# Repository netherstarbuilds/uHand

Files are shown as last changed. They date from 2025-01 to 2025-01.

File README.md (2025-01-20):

# uHand inspired and powered by uMyo

uHand is a full hand manipulator and wrist but not a forearm. uhand requires the user to adapt the WristBracket.SLDPRT file to fit the forearm design they are using. This is as individuals have different amputations and forearm shapes making it not possible to design a one size fits all mount that would work well with this many degrees of freedom. uHand was not made by UltimateRobotics, but was designed to work with their incredible uMyo EMG sensor. uHand requires seven driver motors.

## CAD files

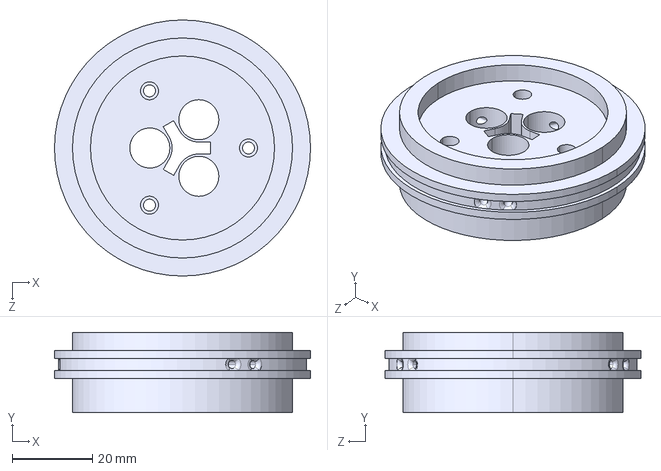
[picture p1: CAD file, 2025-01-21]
mainring.STEP
64.0 x 20.0 x 64.0 mm

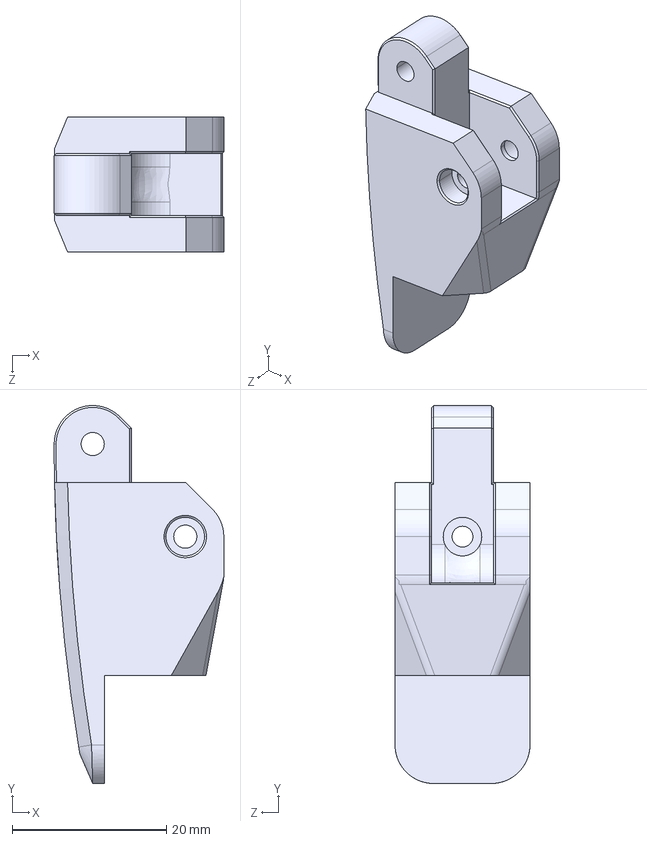
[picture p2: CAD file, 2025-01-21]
DISTAL2T.STEP
22.0 x 49.0 x 17.5 mm

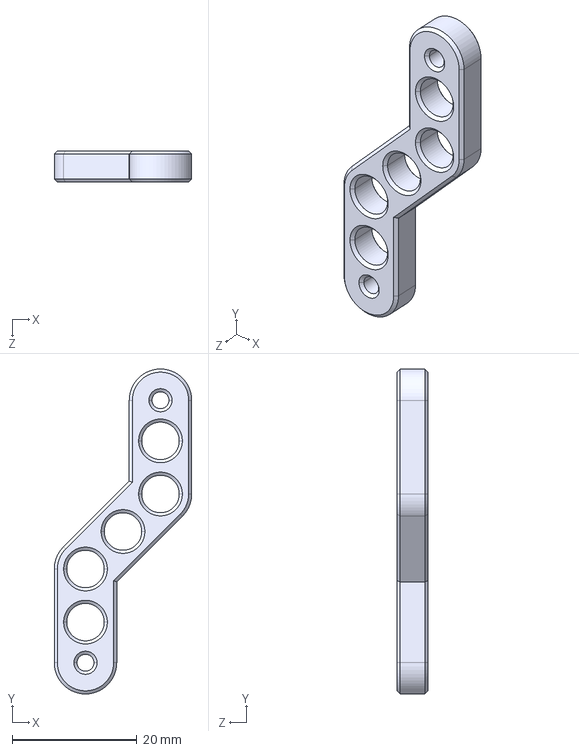
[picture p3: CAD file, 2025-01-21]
crosslinkP1bSTEEL.STEP
22.0 x 52.0 x 5.00 mm

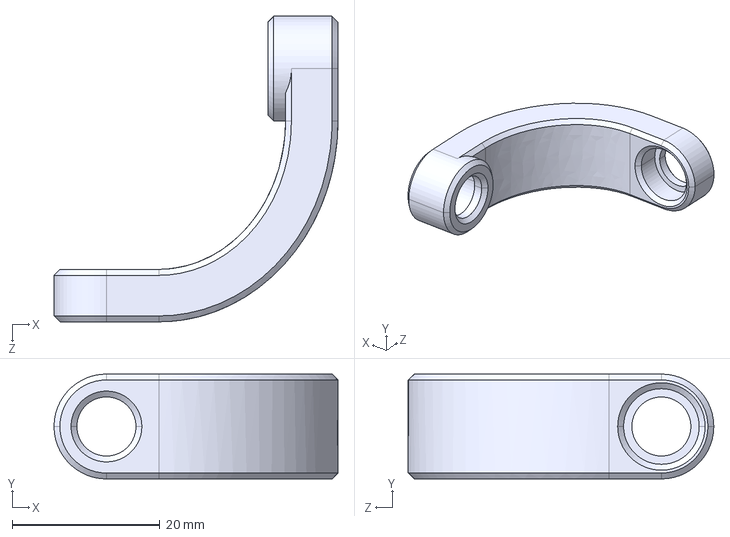
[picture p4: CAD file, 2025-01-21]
SPMbar.STEP
38.5 x 14.2 x 41.4 mm

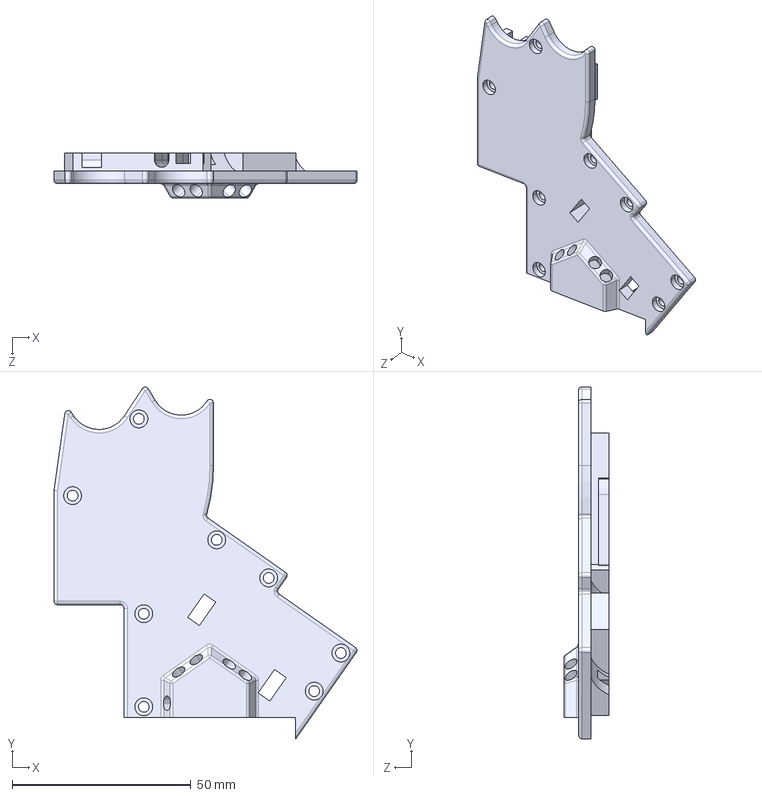
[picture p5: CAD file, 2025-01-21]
PalmPlate.STEP
84.6 x 98.4 x 12.6 mm

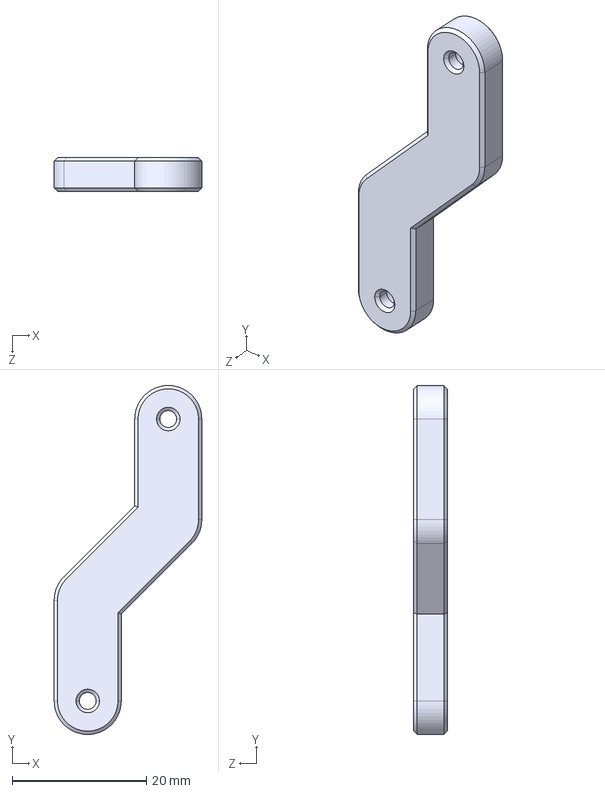
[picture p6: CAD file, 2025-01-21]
crosslinkP1a.STEP
22.0 x 52.0 x 5.00 mm

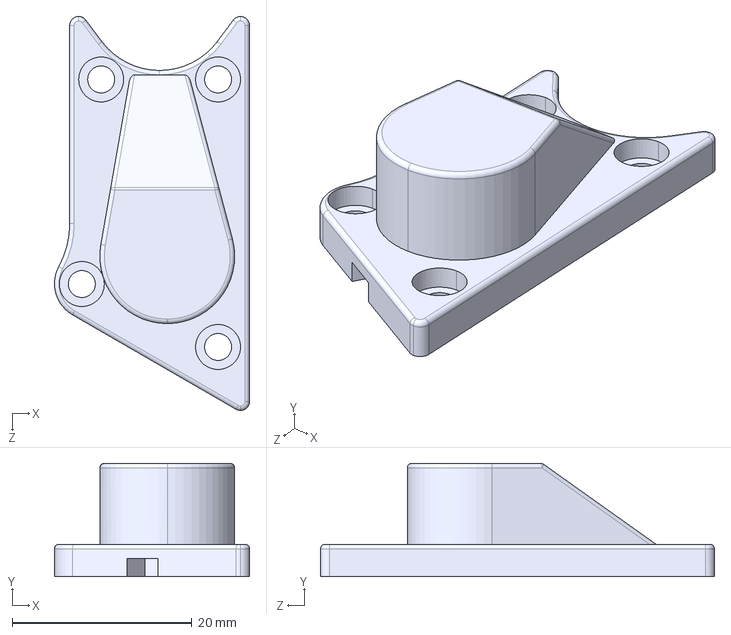
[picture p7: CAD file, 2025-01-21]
metacover.STEP
21.7 x 12.6 x 43.8 mm

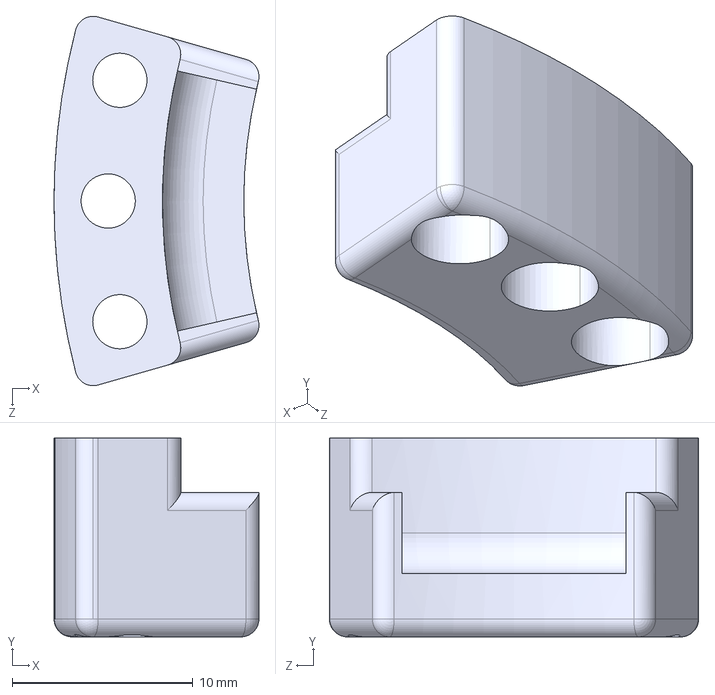
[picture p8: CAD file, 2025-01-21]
PartialBearingB.STEP
11.3 x 11.0 x 20.4 mm

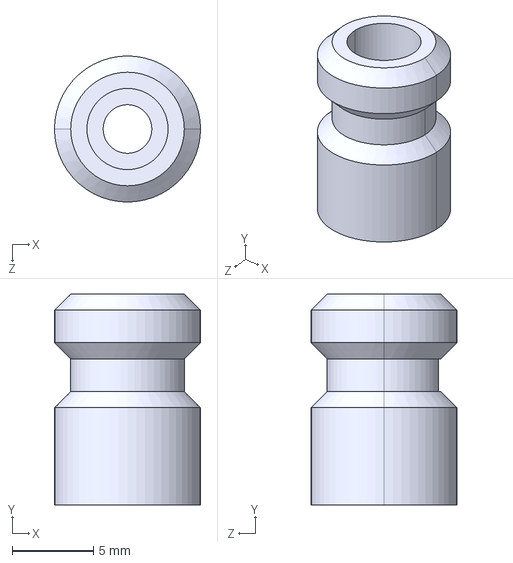
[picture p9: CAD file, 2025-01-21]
WristSpool.STEP
9.00 x 13.0 x 9.00 mm

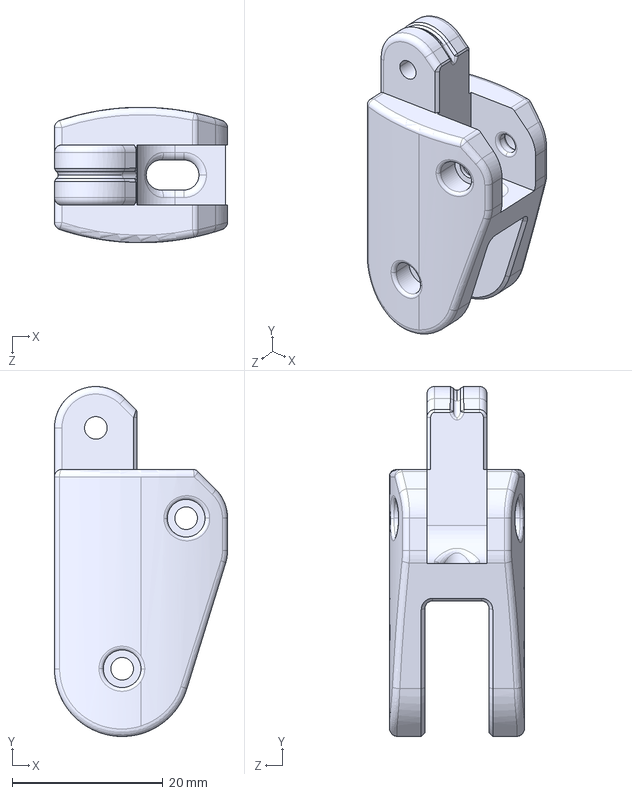
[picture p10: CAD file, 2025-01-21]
PPJOINT.STEP
23.0 x 46.5 x 18.0 mm

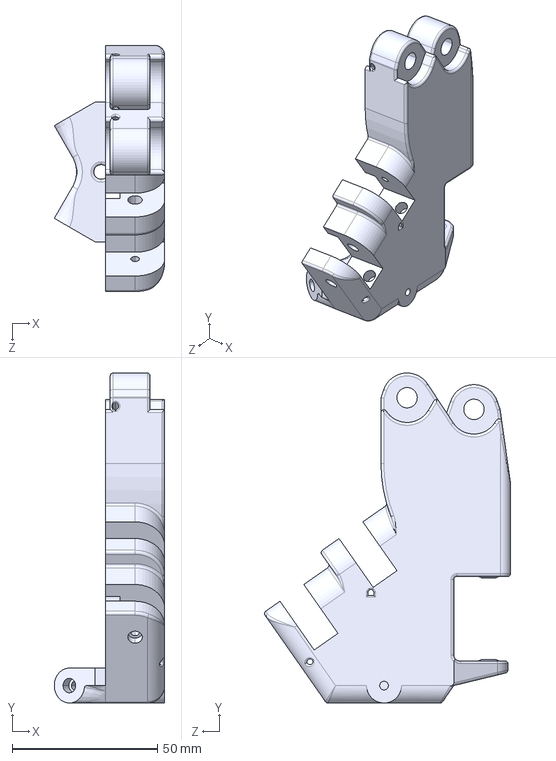
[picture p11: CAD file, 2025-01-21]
12palm.STEP
38.0 x 113.5 x 84.6 mm

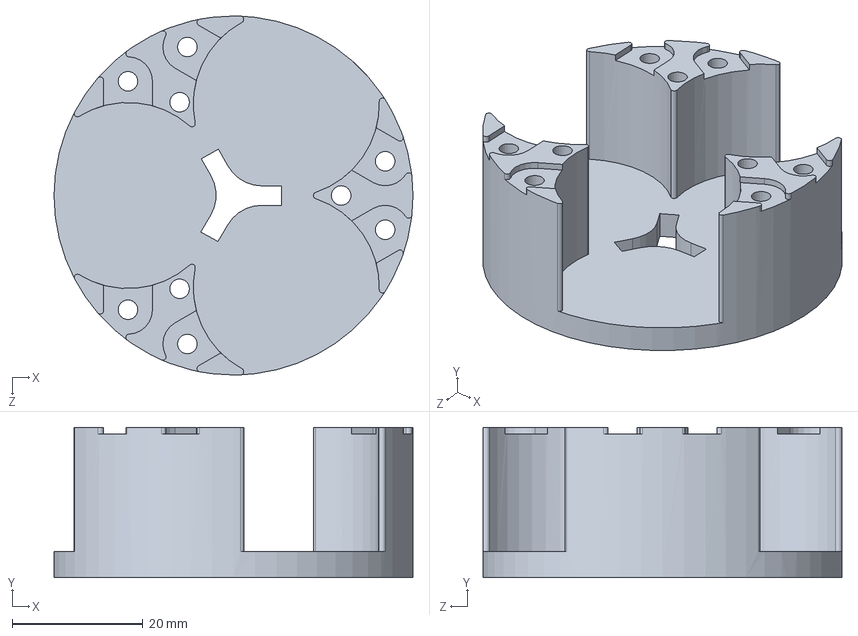
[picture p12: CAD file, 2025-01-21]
WristBracket.SLDPRT
55.0 x 23.0 x 55.0 mm

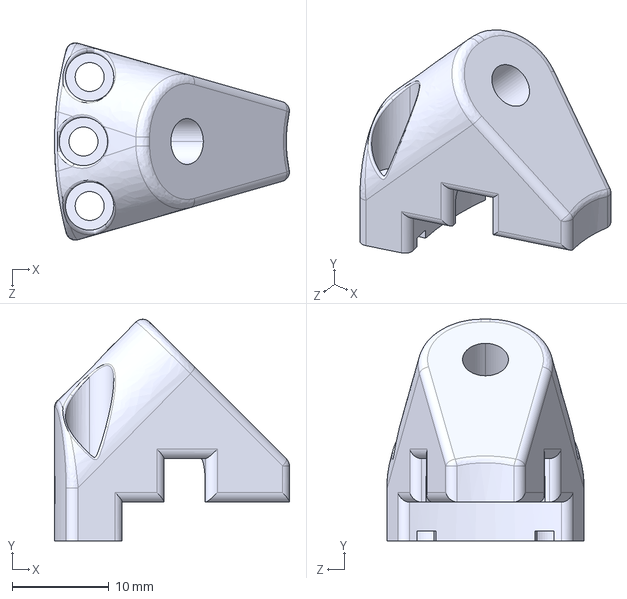
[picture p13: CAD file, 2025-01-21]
PartialBearingA.STEP
24.3 x 22.9 x 20.4 mm

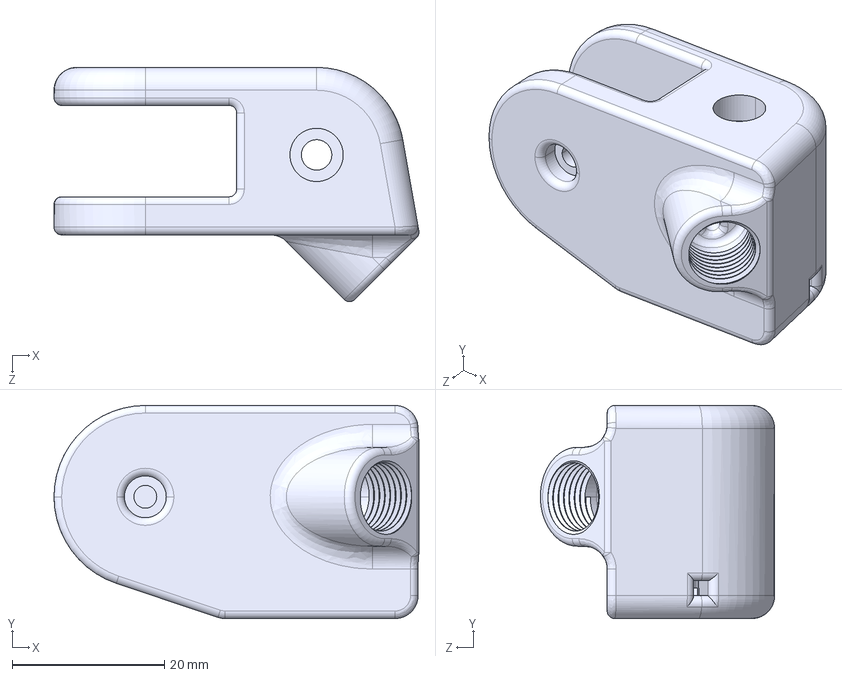
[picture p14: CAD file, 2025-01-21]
TC.STEP
48.0 x 28.0 x 30.8 mm

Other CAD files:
DistalPlate.STL
crosslinkP1b.STEP
crosslinkP2.STEP
META1.STEP
DISTAL2.STEP
MCPJOINT.STEP
Tmeta.STEP
crosslinkP1aSTEEL.STEP
crosslinkP2STEEL.STEP
spool.STEP

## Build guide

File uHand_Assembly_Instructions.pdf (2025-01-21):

Preface
Parts will often be removed in images demonstrating a different part of assembly to make them more clear, the parts are still meant to be in place.

The software is not developed by me but updates on it will be able to be found at https://github.com/Open-Muscle

All bolts are m3 threaded

All servo motors have their mounting brackets cut off by hand

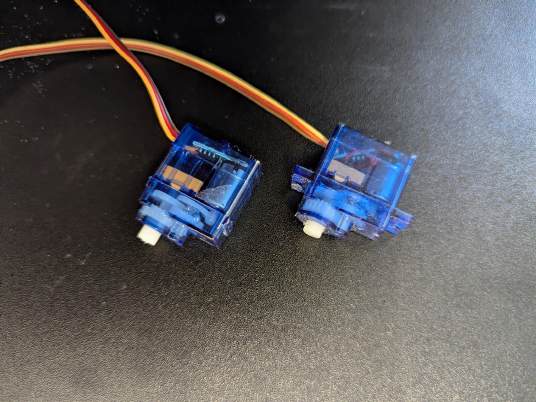
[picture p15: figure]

This document was meant to be viewed without page breaks

Parts needed
(all STEEL part files are alternate designs to be lighter if using SLM printed steel) (all bolts are M3)
12palm.STEP x1
DistalPlate.STL x1
PalmPlate.STEP x1
TC.STEP x1
Tmeta.STEP x1
WristBracket.SLDPRT x1
mainring.STEP x1
DISTAL2T.STEP x1
META1.STEP x2
metacover.STEP x2
PartialBearingA.STEP x3

PartialBearingB.STEP x3
SPMbar.STEP x3
SPMbarSTEEL.STEP x3
WristSpool.STEP x3
DISTAL2.STEP x4
MCPJOINT.STEP x4
PPJOINT.STEP x4
crosslinkP1a.STEP x5
crosslinkP1aSTEEL.STEP x5
crosslinkP1b.STEP x5
crosslinkP1bSTEEL.STEP x5
crosslinkP2.STEP x5
crosslinkP2STEEL.STEP x5
spool.STEP x5

3x3x7 bearing x34
M3 hex nut x4
5x20.5mm spring x6
SG90 servo motor x5
J48 stepper motor x3
3x10x4 bearings 3
6mm bolt x47
10mm bolt x3
15mm bolt x24
18mm bolt x12
20mm bolt x7
25mm bolt x9
35mm bolt x1
100+ m3 heat set inserts (you will need extras for failed prints) 1mm dyneema tendon thread
Bowden tube ptfe tubing
Bowden tube connector x6
4.5mm bbs x24

Assembly
1- Prep one MCPJoint with two heat set inserts

2- Thread the two tendon cables through the front

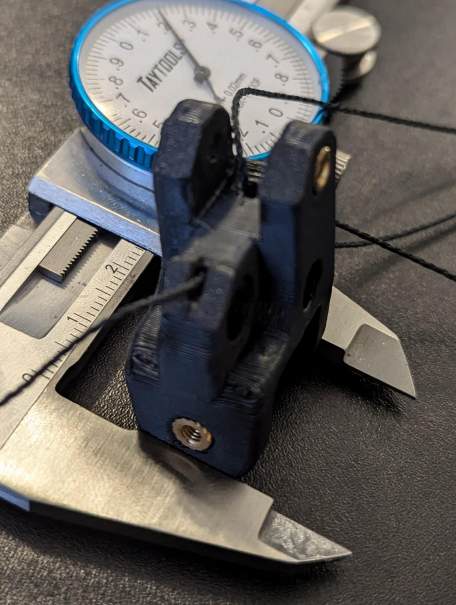
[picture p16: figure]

3- Thread the forward most tendon through the central most hole in one Crosslink2, tie it onto a 6mm bolt and insert the bolt, then embed both parts with 7mm bearings

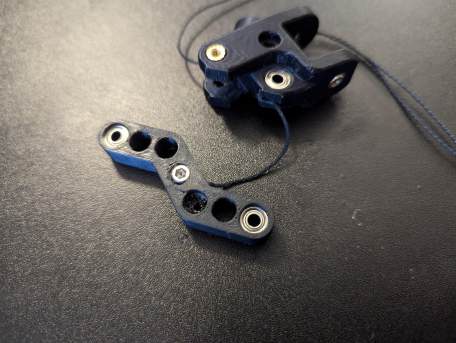
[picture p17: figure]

4- Bolt the two together with 15mm bolts as well as one Crosslink1a and one Crosslink1b (if using metal crosslinks you must also thread the bolt shaft on both Crosslink1a and Crosslink1b)

5- Pull the back tendon over and tie it to one 6mm bolt

6- Then thread another short length of tendon through the last threaded hole in Crosslink2 and tie it on a 6mm bolt once through (better visualization of the process in step 3)

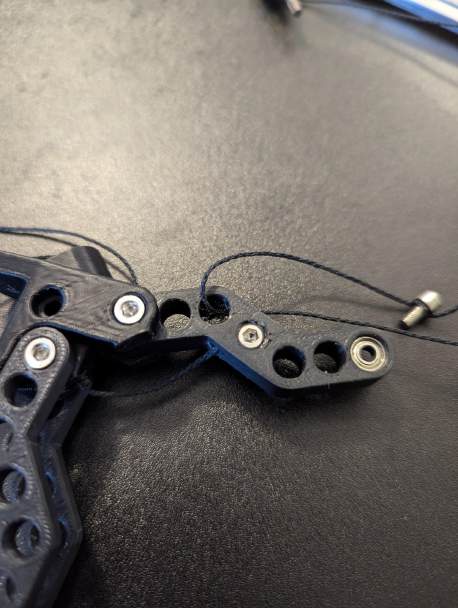
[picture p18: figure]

7- Insert the bolt and file off the back if needed for smooth motion

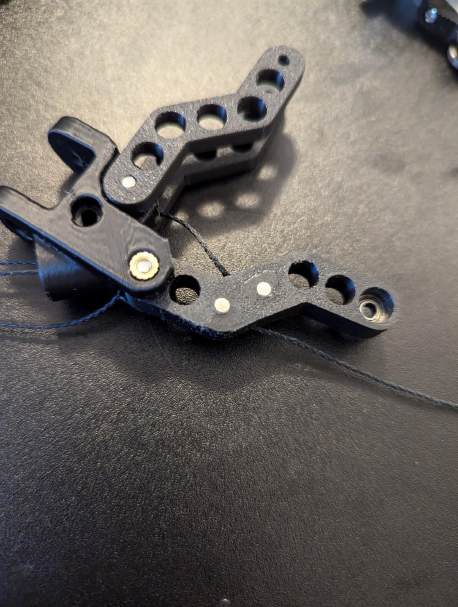
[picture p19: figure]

8- Prep on PPJoint with heat set inserts and a 7mm bearing

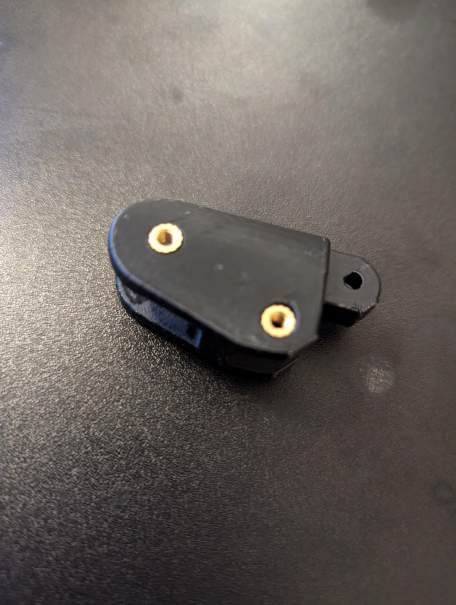
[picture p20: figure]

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
slin

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
ffix

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
10- Prep one Distal2 by CA gluing one distal plate to its top and inserting a 7mm bearing

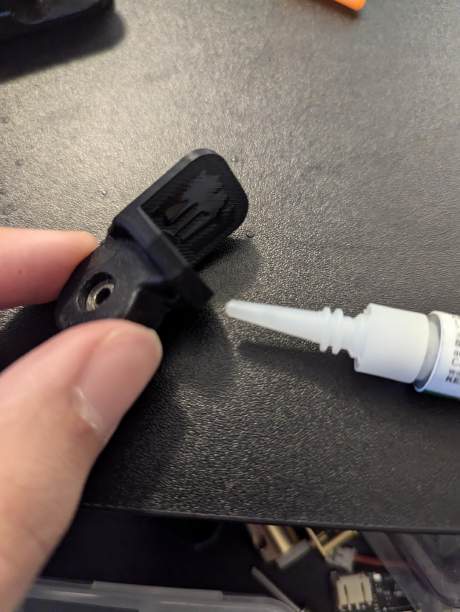
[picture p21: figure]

11- Bolt to PPJoint with one 15mm bolt

12- Thread the topmost tendon through this Distal2

13- Pull tendon taught in a the strait position, loop a 5x20.5mm spring on to a 6mm bolt and drive it into the Distal2’s channel (the distal’s current position will determine its rest state)

14- Tie another 6mm bolt to the tendon from the back of the MCPJoint and bolt the spring down, the finger is done, you can repeat this for the other three

15- Prep 12Palm with heat set insets, bearings, and 4 m3 hex nuts

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
a le

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
ol b

y

b

u

n

c

hin

g it in

t

o

a lo

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
g it
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
ole in

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
ol o

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
w it

d

o

w

n

wit

h it

s in

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
w if necessary

18- Thread the spool loops through the shown channels in the 12Palm

19- Now loop the two tendon threads around the spool a few times in opposite directions (number of loops can be adjusted to modulate range of motion) and slot in the motor

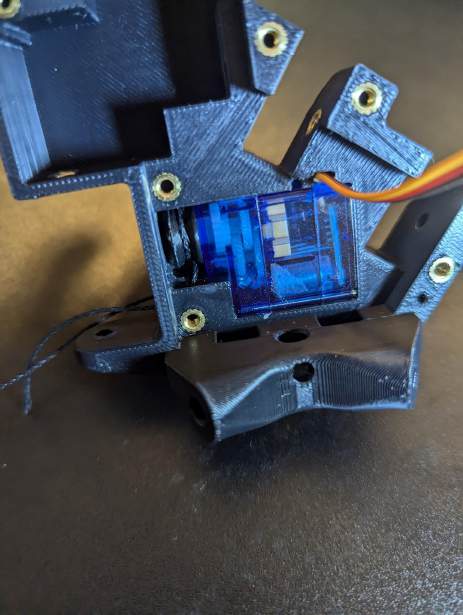
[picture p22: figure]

20- Prep one TMeta and one TC with bearings inserts as shown

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
e, a

t

t

a

c

h

t

w

o le

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
22- Thread tendons through TC channels as shown and bolt them together with an 18mm bolt

23- Now this part is a little awkward but it works, thread the tendons from the servo in the 12Palm through the side channels in the TC and up through the bottom of its shaft hole

24- Run the tendons through the center and embed the bottom 7mm bearing into the TC

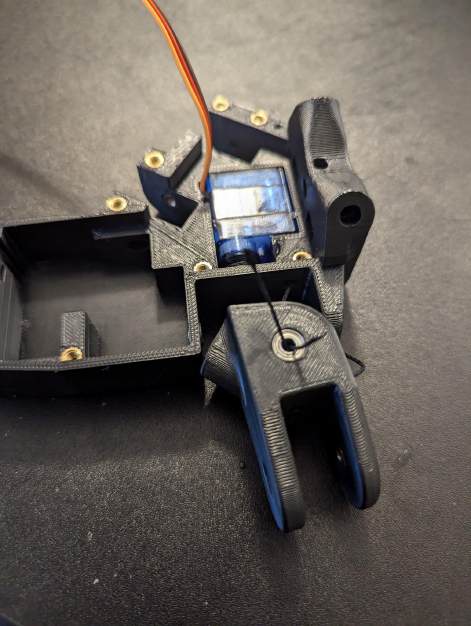
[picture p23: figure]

25- Now run the tendons through the mounting hole in the bracket on the 12Palm and tie them together as hard as you can (once the bolt is in place the TC should not move so preferable use pliers)

26- Drive a 35mm bolt through the bracket and past the tendons (To be careful to not break them you can use a dab of CA glue to keep the tendons in place as long as you are precise as to not glue the bearing)

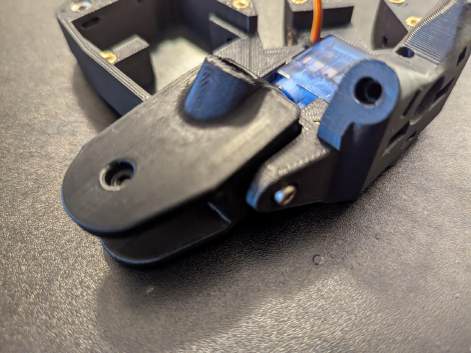
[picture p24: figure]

27- Prep one Meta1 with 5 heat set inserts and one bearing

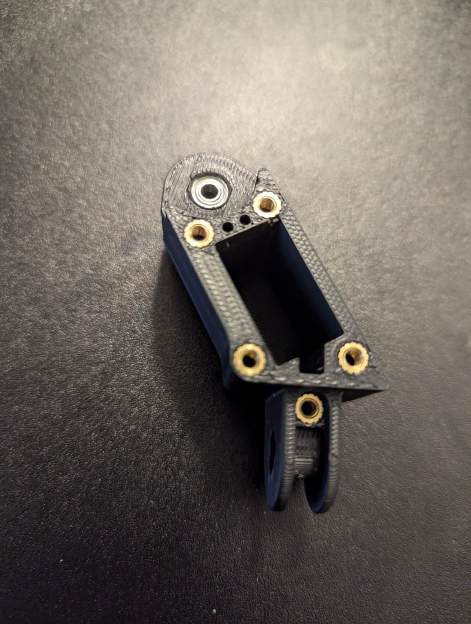
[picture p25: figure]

28- Then insert a servo into the cavity making sure to line the cable up

29- Attach a spool and thread the tendon cables through a MetaPlate (getting angles for this was hard so excuse the photos)

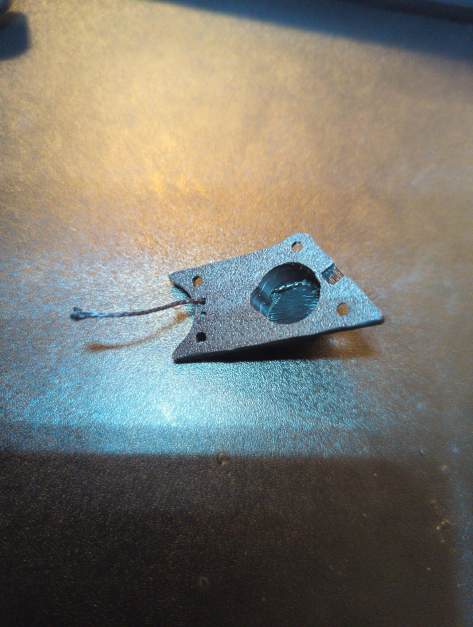
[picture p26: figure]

30- Finally you can bolt down the MetaPlate with 4 6mm bolts

31- Prep the 12Palm by bolting two springs to both metacarpal channels with 6mm bolts

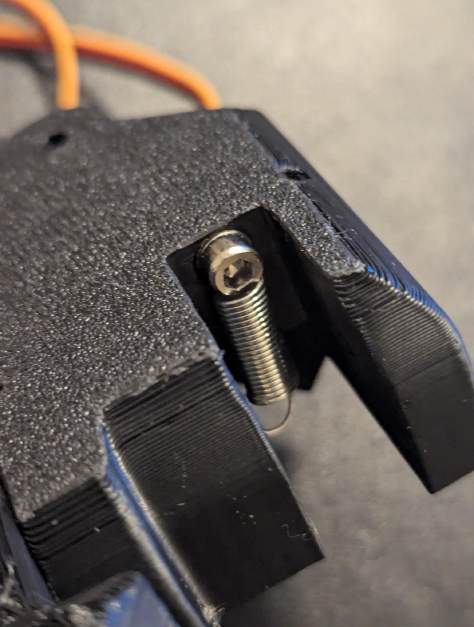
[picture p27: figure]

32- You can now attach the metacarpals to the palm with two 18mm bolts (The mounting hole for the top one has no direct access point so the best way i've found to fasten is it to use force and angle a hex wrench, if anyone can think of a better way please share)

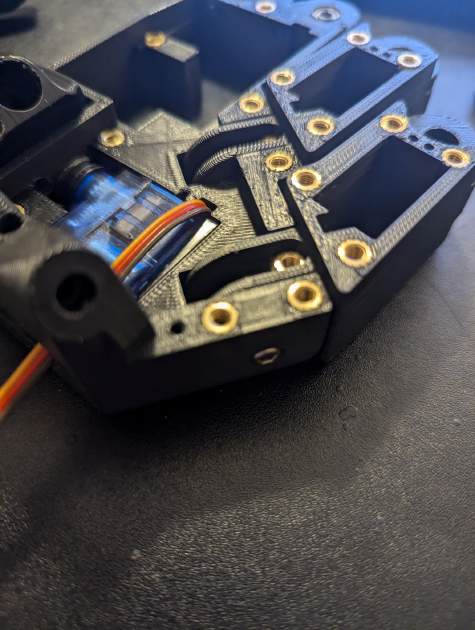
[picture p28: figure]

33- Insert another servo, prepped like the previous one, into the cavity at the top of the 12Palm and bolt down the top of the spring like so

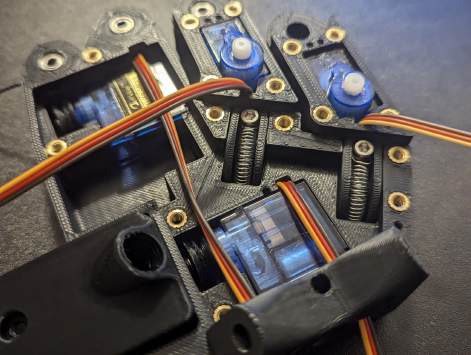
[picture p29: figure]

34- Thread the servo tendons through the MCP bracket on the 12palm

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
d, a

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
olt it

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
36- Install the final servo the same way as the previous one, and repeat this for all the fingers

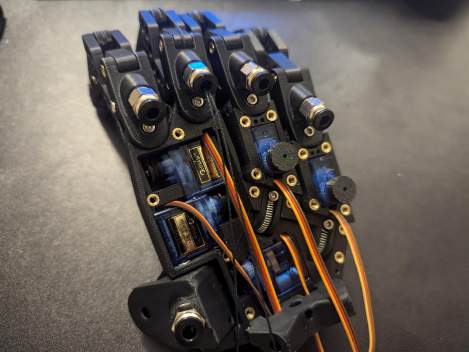
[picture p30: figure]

37- Prep one PalmPlate with a short length of ptfe tubing as shown

38- Route all cables through the Palm Plate, pass the tendons from the central palm servo through the ptfe tubing and bolt the PalmPlate down with 6mm bolts

39- attach a length of tendon cable to both metacarpal bases and thread through the palm (you can check for obstructions with soldering wire, if there are none and the cable won't pass, use more lubricant)

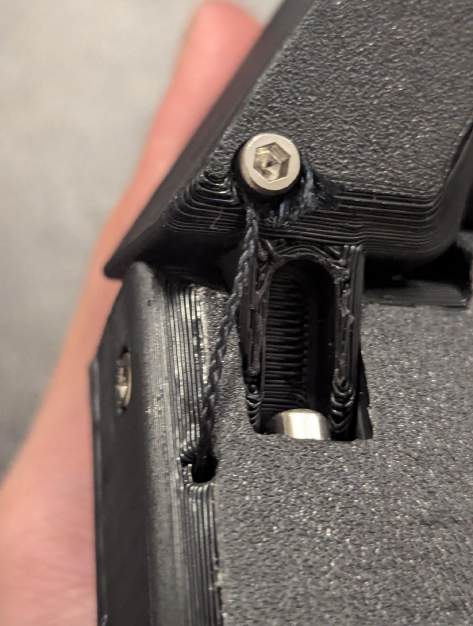
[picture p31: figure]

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
sily

finis

h

e

d in

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
r, min

u

s

t

h

e

dis

t

al tendon.

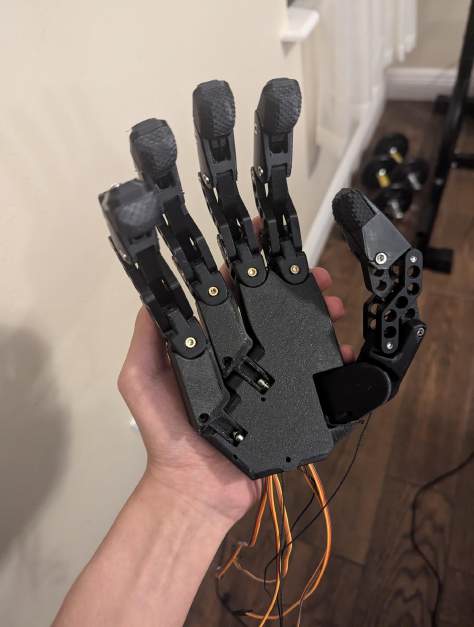
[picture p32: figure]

41- Run all tendons through their respective ptfe tube and coupling and ground the tubes to the hub at the base of the PalmPlate so all tendons pass out of the central bore in the bottom of the 12Palm (CA glue can be used if tubes are not able to friction fit)

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
ol simila

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
a lo

o

p

a

n

d

b

oltin

g it

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
olt.

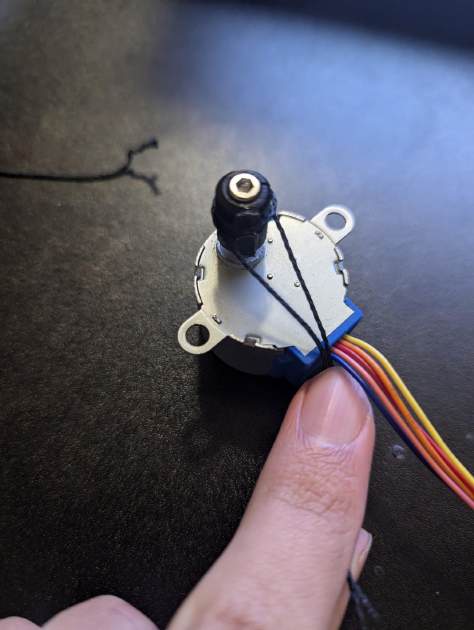
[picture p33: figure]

43- Then prep the MainDisk with inserts and thread the tendons as shown

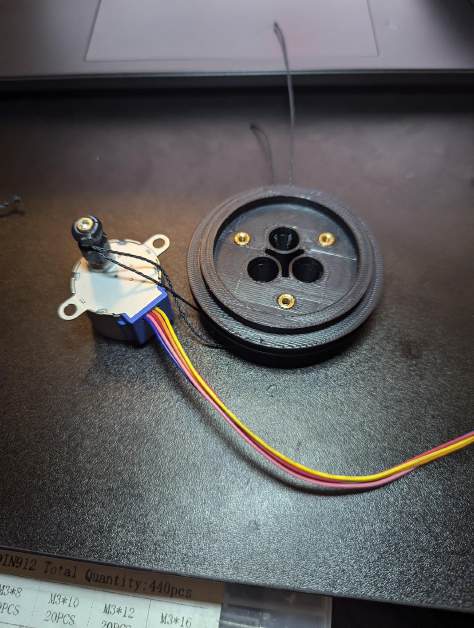
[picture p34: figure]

44- Prep the Partial bearing parts with 4.5mm bbs and inserts

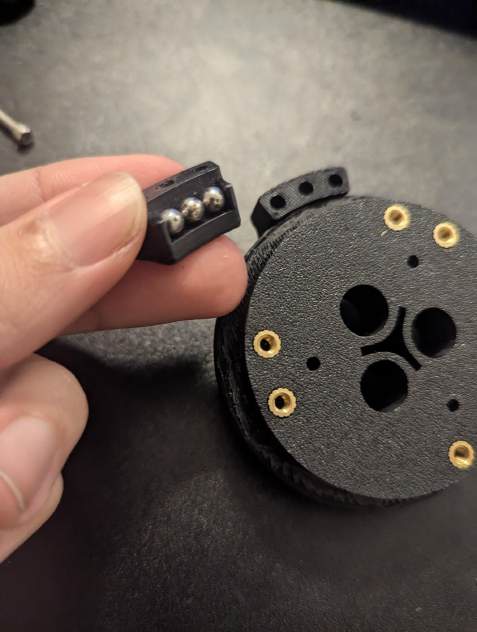
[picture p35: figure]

45- loop and tie the stepper motor tendons to the PartialBearingA as shown

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
t, y

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
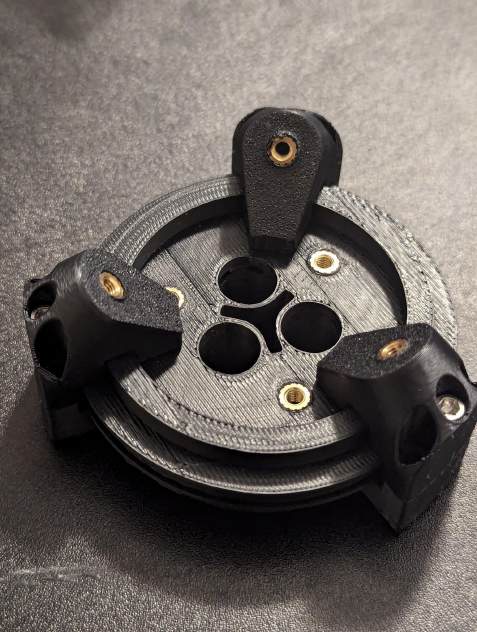
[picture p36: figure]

47- Prep three SPMBar with 3x10x4 bearings and 10mm bolts with hex nuts threaded, and bolt them to the PartialBearing assembly

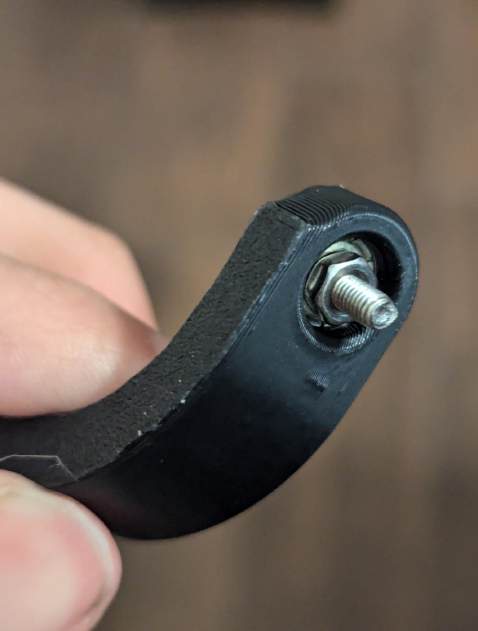
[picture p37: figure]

48- Thread all cables and tendons through the star shaped opening in the MainDisk

49- Bolt the uHand assembly to the wrist with 3 20mm bolts

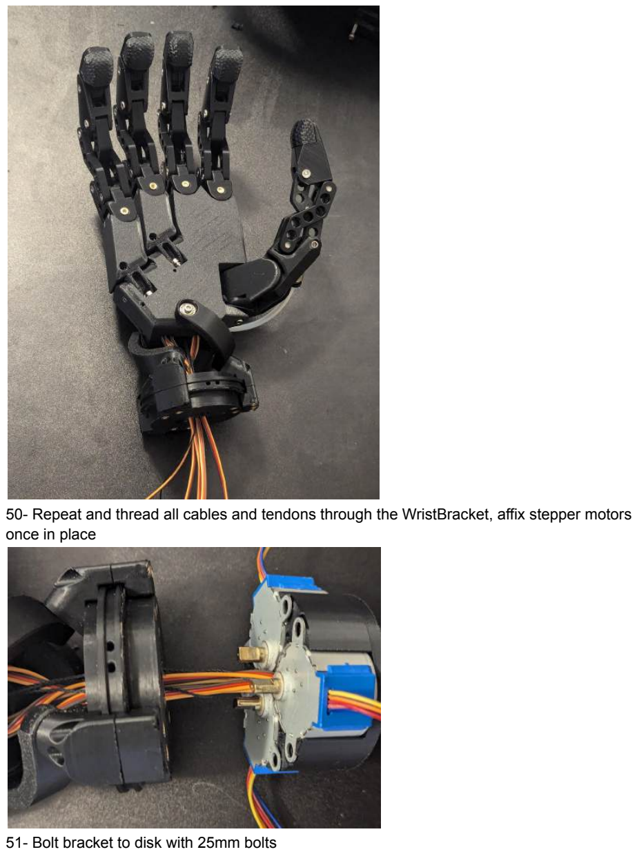
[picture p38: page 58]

50- Repeat and thread all cables and tendons through the WristBracket, affix stepper motors once in place

51- Bolt bracket to disk with 25mm bolts

52- uHand Is Complete!
